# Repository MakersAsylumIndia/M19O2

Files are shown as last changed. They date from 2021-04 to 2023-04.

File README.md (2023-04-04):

# M19O2
DiY Oxygen Concentrator based on / inspired by the [OpenOx](https://github.com/hacklabkyiv/openox), [Marut](https://www.technido.com/marut), [RepRap](https://github.com/RepRapLtd/Oxygen-concentrator) and [Project Apollo](https://github.com/oxycon/ProjectApollo) platforms.

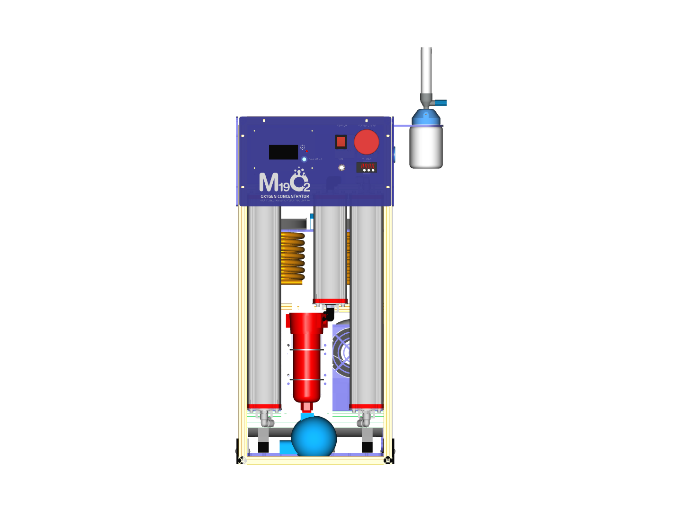
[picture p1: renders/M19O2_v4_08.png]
M19O2 render front


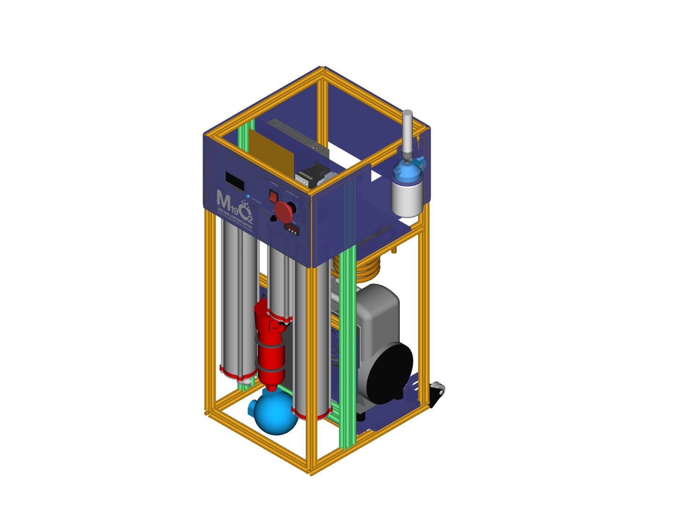
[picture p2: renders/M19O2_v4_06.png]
M19O2 render rear


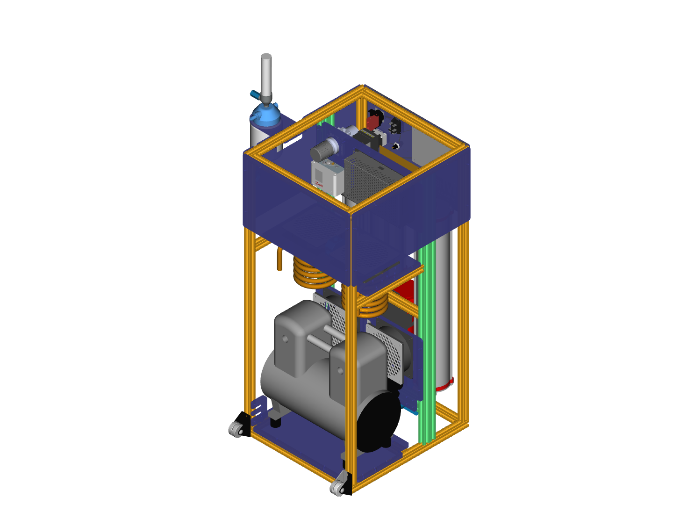
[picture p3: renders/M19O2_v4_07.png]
M19O2 render rear


## About

Read about the project on [Hackaday](https://hackaday.com/2021/04/26/indian-makers-respond-to-the-covid-19-pandemic-by-producing-oxygen-concentrators/).
Also check out the project on the [hackaday.io](https://hackaday.io/project/181201-m19o2-oxygen-concentrator) project page.

The **M19O2** Oxygen Concentrator is "Open Source Hardware" as certified by the [OSHWA](https://certification.oshwa.org/in000029.html).
OSHWA UID for the M19O2 is **IN000029**

<a href="https://certification.oshwa.org/in000029.html">OSHWA UID IN000029

## Contribute

You can contribute on the [Ketto fundraiser page](https://www.ketto.org/fundraiser/m19-oxygen-concentrators-make-in-india)

## Coordination lists

- [Notion workspace](https://www.notion.so/M-19-Collective-b44b9d8d7dd14d5d86d417facf0f4141) for the M19 collective.
- [M19O2 Master](https://docs.google.com/spreadsheets/d/1rJZ5P0rF2Or8yu0H8HEPz25RP8kTAXxbNVU87DqD-eM/edit#gid=0) sheet tracks the city-wise coordinators, tools, FAQs etc.
- [BOM M19O2](https://docs.google.com/spreadsheets/d/1gmmdXTP3EQk-4hCGVYj-FxzUMADlT8mw354VPmYt5A4/edit#gid=870920932) sheet lists the master Bill of Materials (BOM) along with city-wise BOM
- [Starting a community lab](https://docs.google.com/document/d/1oR9rhGmbcnoSBjzQCYwE9Anocvr0q5_VmuVkbnycx18/edit?usp=sharing) document and [Build List for Labs](https://docs.google.com/spreadsheets/d/1DynT9Mh8jcV9qHxwFuQxj1fcQQHj_v_ymwpoZD1L23g/edit?usp=sharing) sheet for lab onboarding information and coordination.

## Engineering

- [Labview testbench](engineering/software/M19-oxygen-concentrator-testbench) is a testbench executable developed by [Fracktal Works](https://github.com/FracktalWorks), useful for tuning the performance of your concentrator prototypes.
- [Computer-aided Design/Engineering](engineering/cad-cae) for design, version control and simulation data related to the M19O2 and its iterations. Committed to open-source and open-innovation.
- [Electronics](engineering/electronics) for all things electronics, including comprehensive design and development data of DIY [Oxygen Analyzers](engineering/electronics/oxygen_analysers) and other [subprojects](engineering/electronics/subprojects).

## How to use this repo

Open a terminal on your computer. Run

```bash
git clone https://github.com/MakersAsylumIndia/M19O2 && cd M19O2
git submodule update --init --recursive
```
The repository shall be available on your computer.
To periodically update the contents,

```bash
cd M19O2
git pull
git submodule update --init --recursive
```

## How to contribute to this repository

Fork this repository. You can find the command for this on the top-right of the webpage. This shall create a personal, updateable copy of this repository on your github account.

On your computer terminal, run

```bash
git clone https://github.com/<your-username>/M19O2 && cd M19O2
git submodule update --init --recursive
```
Add your contributions to this repository and save on github.

```bash
cd M19O2
git add .
git commit -m "<your-commit-message>"
git push origin
```

To contribute your work to the M19 Collective, open your repository in a browser and issue a pull request from your repository to the one at [Makers' Asylum](https://github.com/MakersAsylumIndia).

## License

Licenses

<a href="LICENSE.md">Open Source Licenses Facts</a>

#### Hardware
CERN Open Hardware License Version 2 - Strongly Reciprocal ([CERN-OHL-S-2.0](https://spdx.org/licenses/CERN-OHL-S-2.0.html)).

#### Software
MIT open source [license](http://opensource.org/licenses/MIT).

#### Documentation:
<br />This work is licensed under a <a rel="license" href="http://creativecommons.org/licenses/by/4.0/">Creative Commons Attribution 4.0 International License</a>.

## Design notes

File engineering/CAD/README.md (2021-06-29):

This folder is dedicated to M19O2 CAD files and version-control.

*Starting/Kickoff contents*
M19O2 - 
 * FCstd file (FreeCAD v0.19) and STEP/STL export formats
 * FCstd files for sub-projects such as sieve compression jig, sieve assembly, O2 sensor housing, Humidity sensor housing etc.

Oxikit_v22 - (DEPRECATED and moved to ARCHIVE)
 * F3D file (Fusion 360), 
 * STEP file (converted from F3D),
 * STL file (converted from STEP. for light *3d viewing* only) 
 * FreeCAD document (converted from STEP file. No feature model)

 * All individual OxiKit parts (exported from Fusion) as STEP files.

*TODO*
 * Convert F3D feature model appropriately to FreeCAD. --> Make freecad assembly with step files.
 * Set up framework for newer local design iterations and dimensional variants.
 * Integrate local subassembles/component information and product BoM management

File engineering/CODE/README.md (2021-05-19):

# M19_Oxikit_SD
Software development
Git submodule for M19 software development.
 
Submodule is currently in argo-1 repositories.

 *TODO General*
 * Create submodules under MakersAsylum git. Current submodules are linked to argo-1 repos. Argo-1, and others, can thereafter fork the submodules for their own development from MakersAsylum.
 * Add all software dev work here.

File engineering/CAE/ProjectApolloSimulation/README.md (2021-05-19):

Note: this repository contains the simulation code for Project Apollo

Please refer to the original repository for more details on Apollo: https://github.com/oxycon/ProjectApollo 

These files are for a simulation of pressure swing adsorption oxygen concentrator

# References

For numerical methods:
Haghpanah, et al "Multiobjective Optimization of a Four-Step Adsorption Process
for Postcombustion CO2 Capture Via Finite Volume Simulation"  Industrial & Engineering
Chemistry Research, 2013

For PSA operation:
Farooq, "Numerical Simulation of a Pressure Swing Adsorption Oxygen Unit"
Chemical Engineering Science, Vol 44, No 12, pp 2809-2816, 1989.

For constants for sieve material 5A and 13X
Mofarahi, "Comparision of Two Pressure Swing Adsorption Processes for Air Separation
Using Zeolite 5A and Zeolite 13X", Petroleum & Coal,  ISSN 1337-7027, 55 (3) 216-225, 2013.

# Software organization
```
psa.py         simulation module - provides a function simulate() and simulate_and_plot()
               which can be called to do the acutal simulation
params.py       sets the parameters (other files are available: params-apollo, etc.)
mylog.py       log file utilities
difference.py  finite volume and finite difference functions
simple_sim     early simulation that does not do any adsorption (ignore)
```
# Top level files
```
(these call simulate_and_plot() ) and run from the command line.
Use standard python command line options, use --h for help
single_sim     does a single simulation, demostrates usage of simulate_and_plot
optimize       Uses scipy optimization routines to optimize variable through search
annealing      Uses simulated annealing technique for same
monte_sim      Uses Monte Carlo technique for same
multiple_sim   Does a range of simulations
search_sim     Similar, tries to capture best result
jee_sim        Simulation of Jee paper parameters
```

# State Vars
The state variables in the system are:
For each container (1 and 2), each state variable in an (N,) array, where
N (=param.N) is the number of cells in the discretization of the PDE.  10 cells
works well, although higher accuracy is obtained with a much larger number.  All
the variables are in dimensionless values, that are normalized to generally be from
0-1, although they could exceed that.  For example, time is normalized so that the
initial velocity air flow takes 1 unit of time to travel across the container
bed, but the simulation might run for 100's of units of time.
```
   P:  Pressure of gas in bed
   T:  Temperature in bed (this version uses a contant T)
   Tw: Temperature of wall of bed (this version uses a constant Tw)
   xA: Adsorbed amount (mass/volume) of component A (Oxygen)
   xB: Adsorbed amount (mass/volume) of component B (Nitrogen)
   yA: partial concentration of component A (Oxygen) in bed (fraction 0-1)
   yB: partial concentration of component B (Nitrogen) in bed (fraction 0-1)
```
The product tank has 2 state variables:
```
  Pprod:  Pressure in tank
  yprod:  fraction of Oxygen in tank
```
# Modes
We have 6 modes to operate under:
```
                            COL1                    COL2
MODE     Switch 5-way valve                            
half==0 and 1.   Pressurize 1           pressurizing              Vent
half==0 and 2.   Produce 1              pressurize & output       Vent
Open cross valve
half==0 and 3.   CrossVent              Pressurize, out to COL2   Vent
Close Cross valve and Switch 5-way valve
half==1 and 1.   Pressure 2
half==1 and 2.   Produce 2
Open cross valve
half==1 and 3.   CrossVent 2
and repeat at top
```

# Observations

1. The cycle time must be short enough that the product (O2) tank can supply the
   desired flow rate without dropping the pressure too much.  At 5 LPM, a 2L tank
   at 3 bar abs can hold about 2*2/5*60 sec of product (48 sec).
2. The absorption rate of the seive material affects the rate of pressure growth
   in the tanks.  Thus the cycle time is dependent on the absorption rate of the
   material
3. A shorter cycle time could work, but the oxygen level grows slower (in cycles),
   as the pressure does not reach feed pressure by the end of the cycle (unless
   a larger orifice is used).  This might be OK, it just takes more than 7 cycles
   to reach steady state.
   See sims for 10 sec (real) cycle

# NOTES
You can use Inkscape to view and convert svg files. inkview comes with inkscape.

inkview <svg-files>
inkscape -z -w <width-in-pixels> -h <height-in-pixels> <svg-file> -e <png-file-name>

Inviracare XL cylinders are D=.083m, L=.355m
2 Liter bottle: D=0.10, L=.33

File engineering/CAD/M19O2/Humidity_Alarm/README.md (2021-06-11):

# M19O2 Humidity Alarm

  Reads a DHT-22 sensor attached in-line between the output of Dessicant Sieve and input of high pressure regulator of the M19O2 Oxygen Concentrator.
  This tells us how much moisture is entering the Zeolite Dessicant Sieves.
  
  * HIGH = >50%rH = Red Blinking LED + Buzzer
  * MID = <50%rH, >30%rH = Red Blinking LED
  * LOW = <30%rH, >15%rH = Blinking Green LED
  * AWESOME = <15%rH = Steady Green LED

  The DHT22 can only measure under ambient pressure (1 ATM), so we tap off the high pressure line and feed air through restrictors (orifices) in to an air-sealed chamber containing the DHT-22.
  The output from the air sealed chamber feeds back in to the main line, again through a similar restrictor orifice.

  In a later iteration, a flushing solenoid valve can be connected which will purge incomming air back to atmosphere until humidity level falls below a set percentage, thus preventing humid air from reaching the sieves.

  This code is in the public domain.

  Hardware and code by Anool J M (@anool) and Narender Sharma of Maker's Asylum  

  https://github.com/MakersAsylumIndia/M19_OxiKit/tree/main/engineering/M19Oxykit_humidity_alarm

=======

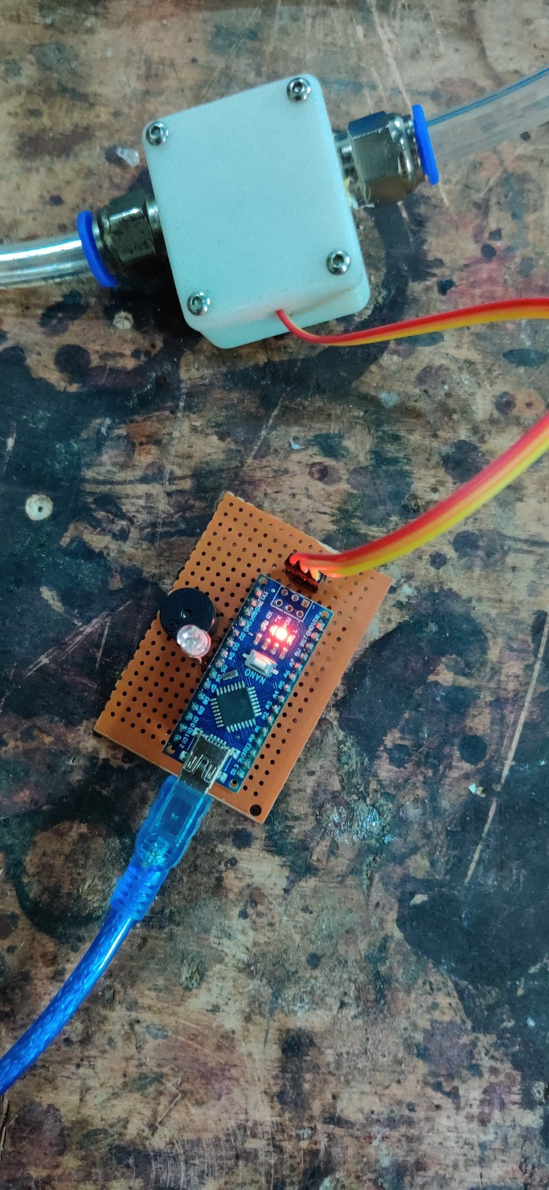
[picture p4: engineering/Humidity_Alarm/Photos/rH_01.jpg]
Humidity Alarm photo 1


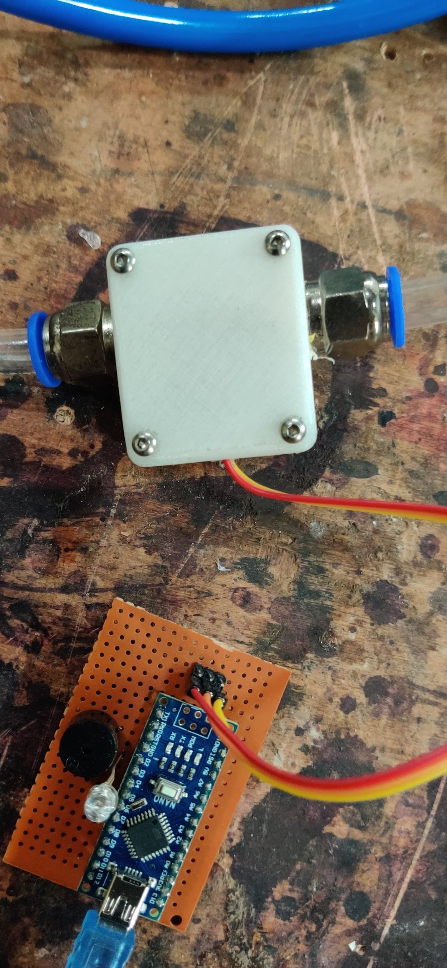
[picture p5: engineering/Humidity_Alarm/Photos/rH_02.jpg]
Humidity Alarm photo 2


License
-------
[CERN Open Hardware Licence v1.2 ]

[CERN Open Hardware Licence v1.2 ]:http://www.ohwr.org/attachments/2388/cern_ohl_v_1_2.txt

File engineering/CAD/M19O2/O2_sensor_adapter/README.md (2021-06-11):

# M19O2 Oxygen Sensor Adapter

  3D printed adaptor to connect an Envitec OOM-Series O2 sensor at the output of the M19O2 Oxygen Concentrator
  
  This design is in the public domain.

  Hardware design by Anool J M (@anool) of Maker's Asylum.

  https://github.com/MakersAsylumIndia/M19_OxiKit/tree/main/engineering/O2_sensor_adapter

=======

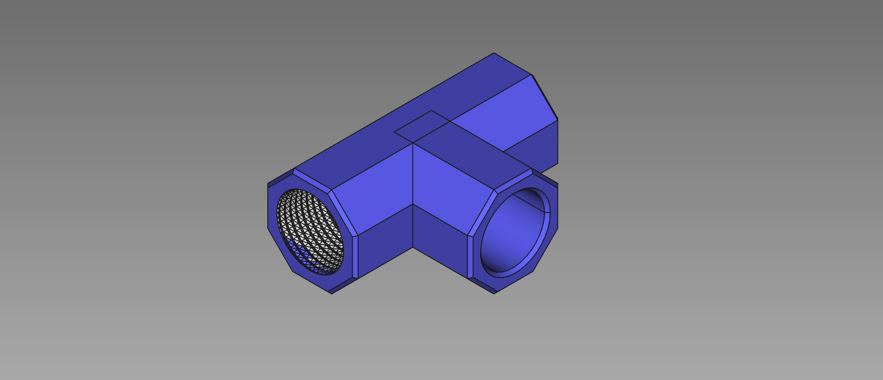
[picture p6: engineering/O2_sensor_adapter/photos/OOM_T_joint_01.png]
O2 sensor mount photo 1


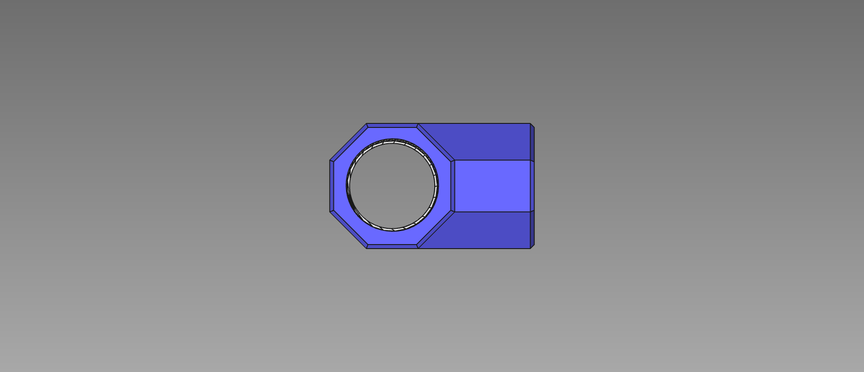
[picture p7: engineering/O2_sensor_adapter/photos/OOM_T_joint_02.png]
O2 sensor mount photo 2


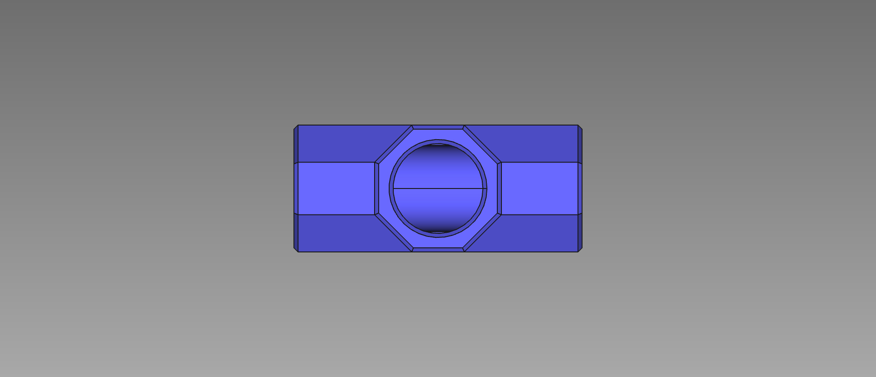
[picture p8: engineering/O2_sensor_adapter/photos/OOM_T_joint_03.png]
O2 sensor mount photo 3


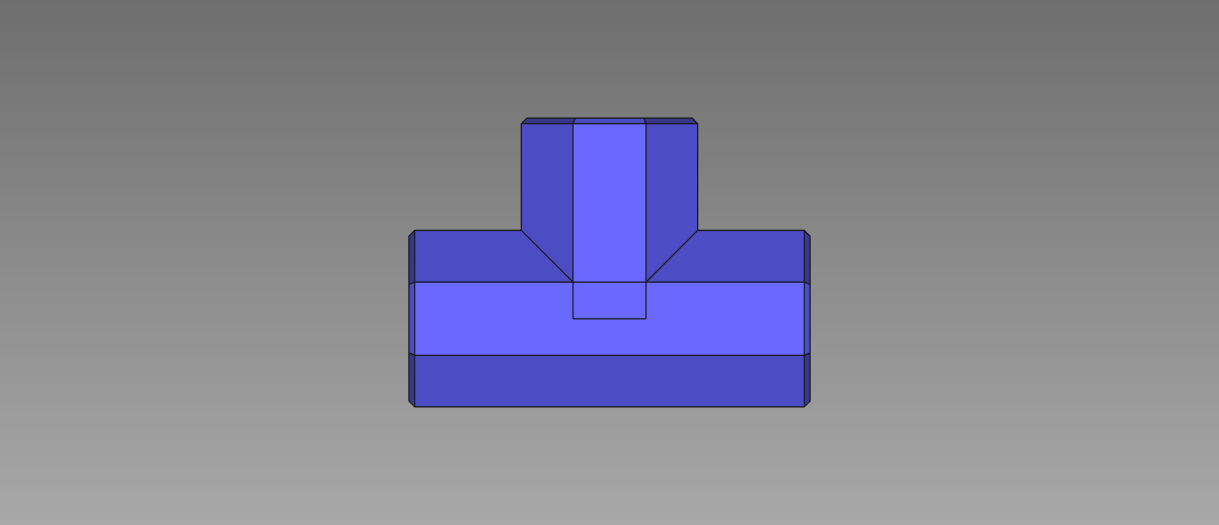
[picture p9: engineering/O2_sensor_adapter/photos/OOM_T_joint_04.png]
O2 sensor mount photo 4


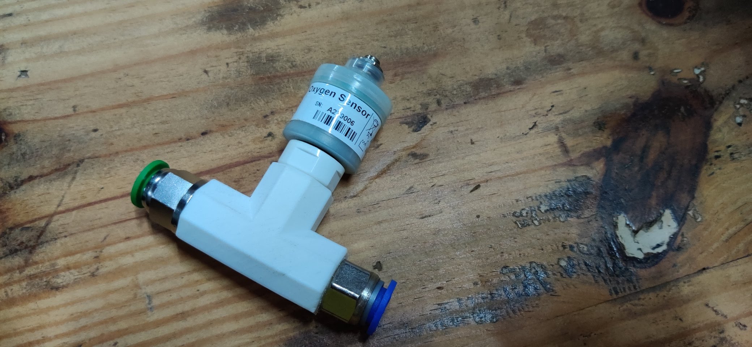
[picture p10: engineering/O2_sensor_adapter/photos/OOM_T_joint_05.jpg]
O2 sensor mount photo 5


License
-------
[CERN Open Hardware Licence v1.2 ]

[CERN Open Hardware Licence v1.2 ]:http://www.ohwr.org/attachments/2388/cern_ohl_v_1_2.txt

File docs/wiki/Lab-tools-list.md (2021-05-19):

## Tools list for labs

This list is curated from the [Lab Tools Requirement](https://docs.google.com/spreadsheets/d/1DynT9Mh8jcV9qHxwFuQxj1fcQQHj_v_ymwpoZD1L23g/edit#gid=1782181776) sheet.

Contributions to improve this Wiki page are welcome.

TODO: add e-store links to each tool.

| Tool Name | Required for process | Alternative tools | Notes | Video Reference | Image Reference |
| ------ | ------ | ------ | ------ | ------ | ------ |
| Oxygen Analyzer | Quality Assurance  |  | Ensure Quality of oxygen (% concentration)  meets requirements. Also ensure both sieves are working at expected | [https://www.youtube.com/watch?v=cm3BnYiPxQ0](https://www.youtube.com/watch?v=cm3BnYiPxQ0) |  [https://tinyurl.com/Oxygen-Testor](https://tinyurl.com/Oxygen-Testor)|
| Electric Sander | Cleaning/smoothing wood and PVC parts | Sand paper/ Emery paper | Sand paper (for wood, PVC, various grits) and Emery paper (for metal, various grits) |  | |
| Soldering Iron | Electronics / Electrical wiring | Solder Station |  |  |  |
| Electrical Tape | for insulation of wire joints | [Wire Nut / Wire Connector](https://en.wikipedia.org/wiki/Twist-on_wire_connector) |  |  |  |
| Electrical Drill | Wood work  | Hand drill |  |  |  |
| Drill Bits- various sizes | Wood work  |  |  |  |  |
| 1" Forschener Bit | for making large holes in wood | aka Hole saw / Hole cutter etc |  |  |  |
| Safety Equipment |  |  | Gloves, Eye glasses etc |  |  |
| Wire Strippers | Electronics / Electrical wiring |  |  |  |  |
| Screw Drivers | Assembly |  |  |  |  |
| Wrenches | Assembly |  |  |  |  |
| Plumbers Tape | for thread sealing of pneumatic fittings | aka Teflon Tape |  |  |  |
| Tubing Cutter | flexible pneumatic tube cutting |  |  |  |  |
| Saw for PVC Cutting | PVC cutting |  |  |  |  |
| Hose Clamps |  |  |  |  |  |
| PPE Kit for build team |  |  |  |  |  |
| Table for build |  |  |  |  |  |
| Electrical extensions with multi plug |  |  |  |  |  |
| General purpose knife / box cutter etc | Multiple |  |  |  |  |
| Deburring tool | For deburring cut PVC pipes | general purpose knife or sand paper |  |  |  |
| Cleaning cloth rags | Multiple |  | to wipe excess glue and keep things clean |  |  |
| Rubber Gloves | PVC parts assembly |  |  |  |  |
| Adjustable spanner / pipe wrench | PVC parts assembly | cloth + welding gloves + brute strength |capable of 3" piping work  |  |  |
| Adjustable Strap wrench | PVC parts assembly | cloth + welding gloves + brute strength | aka Belt Wrench |  |  |
| Snipper clips (Tin snipper) | PVC parts assembly |  | for cutting 3" drain to size. Not neded if those parts are 3D printed |  |  |
| Scissors | Multiple |  |  |  |  |
| SuperGlue | PVC parts assembly |  | for attaching mesh |  |  |
| Vernier Caliper | Sieve assembly |  | to mark level upto which Zeolite needs to be filled (after comaction) | [https://youtu.be/kibjku2GYq0?t=257](https://youtu.be/kibjku2GYq0?t=257) |  |
| Vibratory mechanism  | Zeolite compaction |  | Many approaches to this - use a pneumatic impact hammer, a vibratory table, any reciprocating hand tool (sander, buffing etc).  Vacuum also works well - using either a Shop Vac or maybe a regular vacuum cleaner) | [https://youtu.be/kibjku2GYq0?t=441](https://youtu.be/kibjku2GYq0?t=441) |  |

Ported by [@nirmaljeffrey](https://github.com/nirmaljeffrey).

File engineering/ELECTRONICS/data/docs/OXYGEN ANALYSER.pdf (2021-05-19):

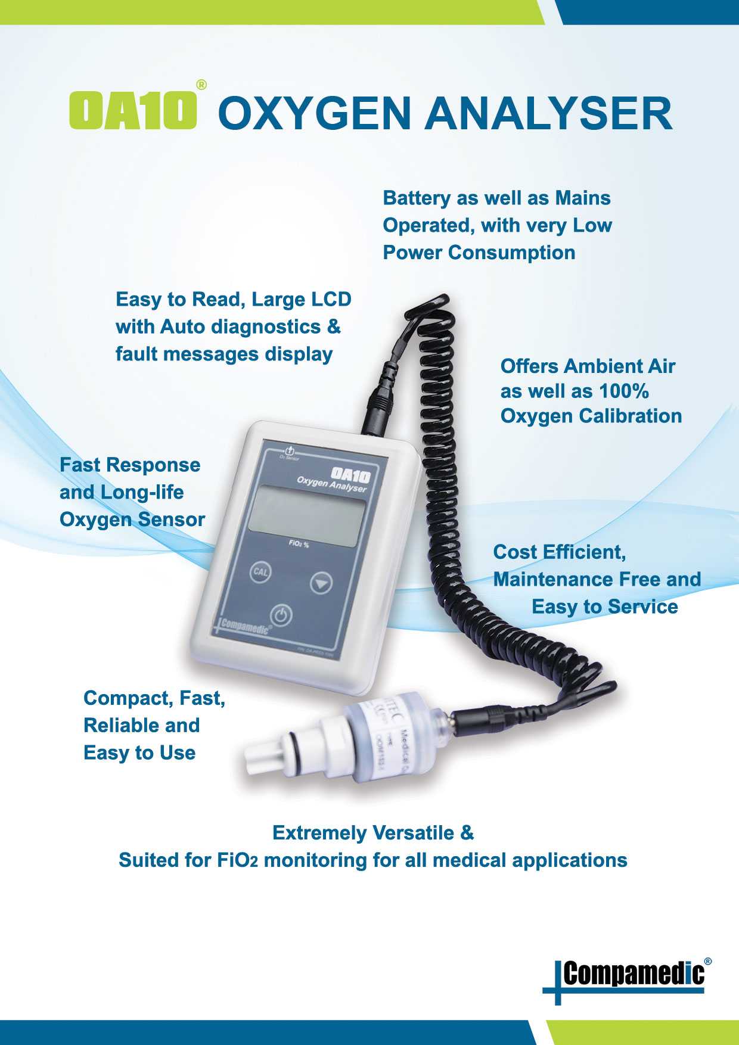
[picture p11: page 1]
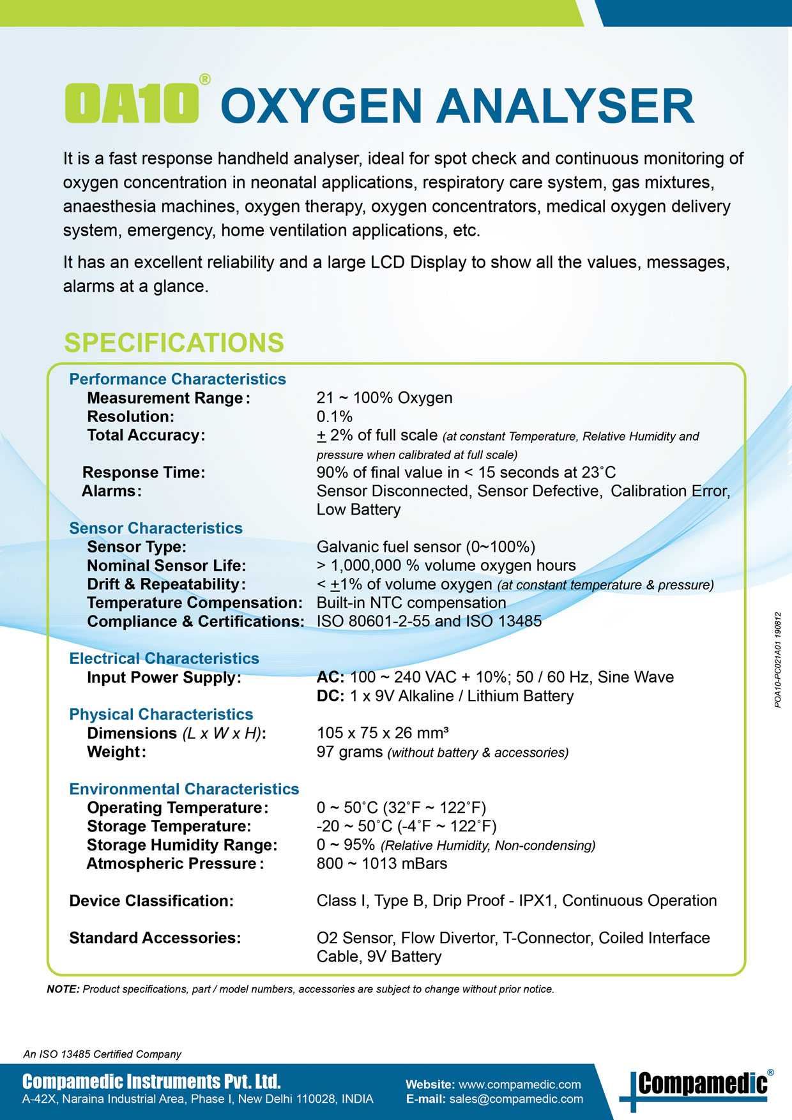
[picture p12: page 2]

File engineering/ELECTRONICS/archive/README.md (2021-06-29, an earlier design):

# Oxikit_Brain_Wiring_Simplified

### This is the simplified schematic for understanding the OxiKit Brain Circuit(Microcontroller based Controller for Oxikit Oxygen Concentrator).

### ECAD Software Used: KiCAD (Open Source ECAD Software)

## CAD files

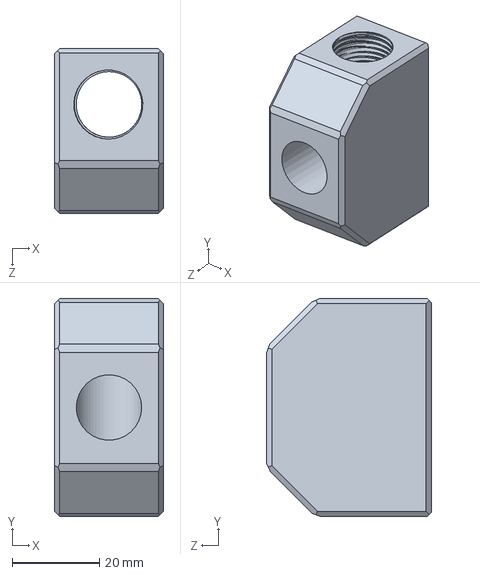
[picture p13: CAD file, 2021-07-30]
engineering/CAD/M19O2/O2_sensor_adapter/T-joint_Vaibhav/M19O2_v4_assembly-O2_sensor.SLDPRT
25.0 x 50.0 x 37.8 mm

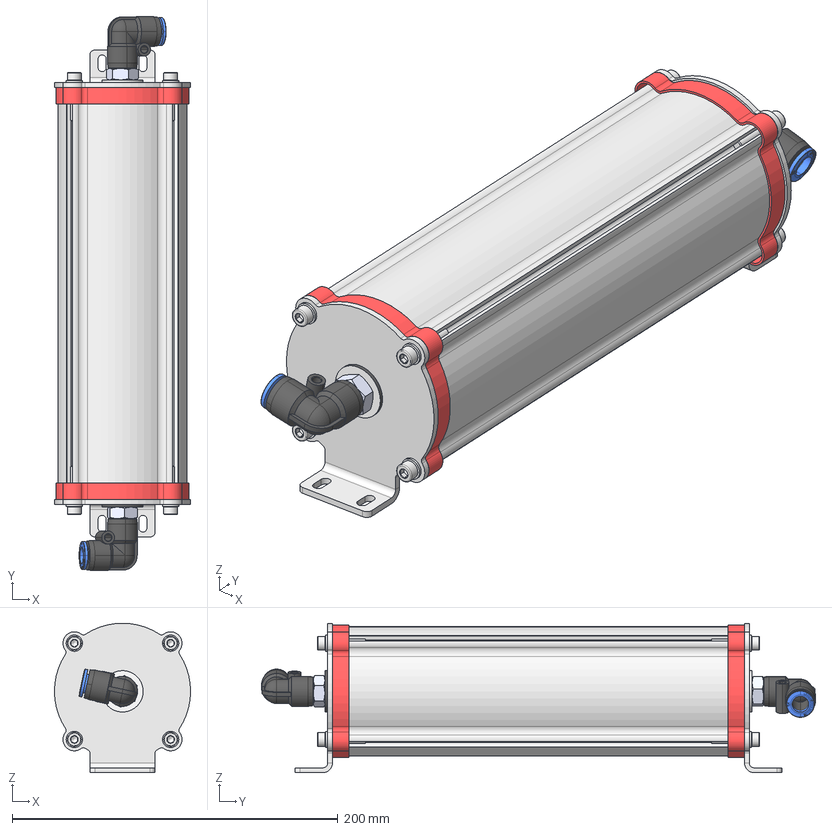
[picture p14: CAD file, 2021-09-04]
engineering/CAD/M19O2/Sieve_Assembly/surge_tank_assy.step
83.6 x 340.2 x 91.8 mm
sieve_body
screws
gasket_(Mirror_#4)
gasket
screws001

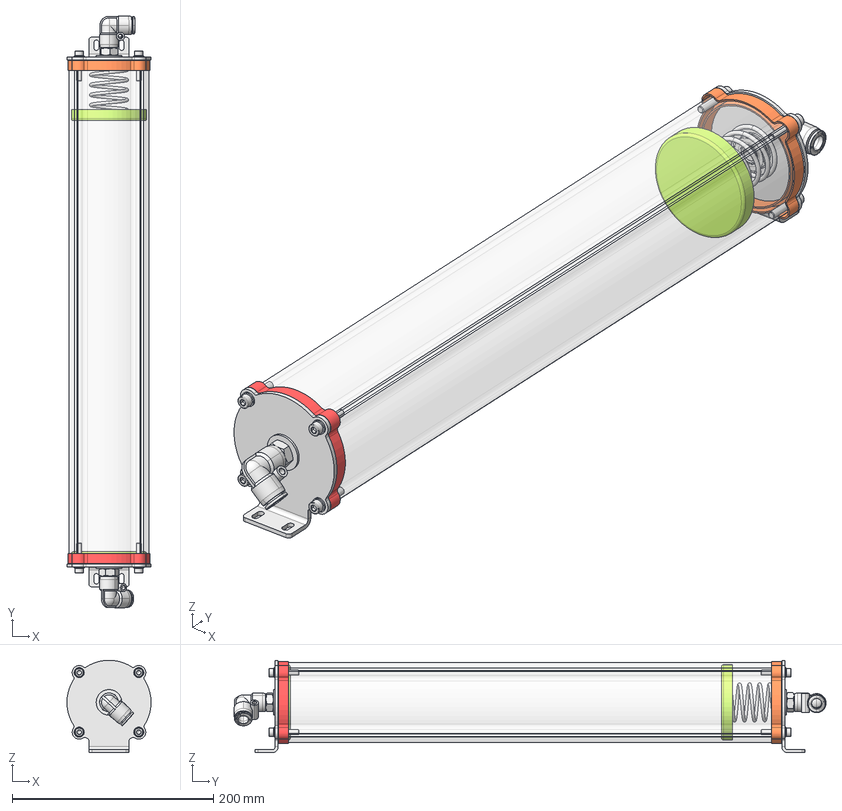
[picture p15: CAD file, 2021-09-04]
engineering/CAD/M19O2/Sieve_Assembly/sieve_assembly_v3.FCStd
83.6 x 587.8 x 91.8 mm
feltpad_filter
feltpad_filter (Mirror #3)
gasket
sieve_body
endcap
drain_cover
drain_cover (Mirror #4)
endcap (Mirror #4)
gasket (Mirror #4)
screws
screws001
endcap_fittings
endcap_fittings001
Spring

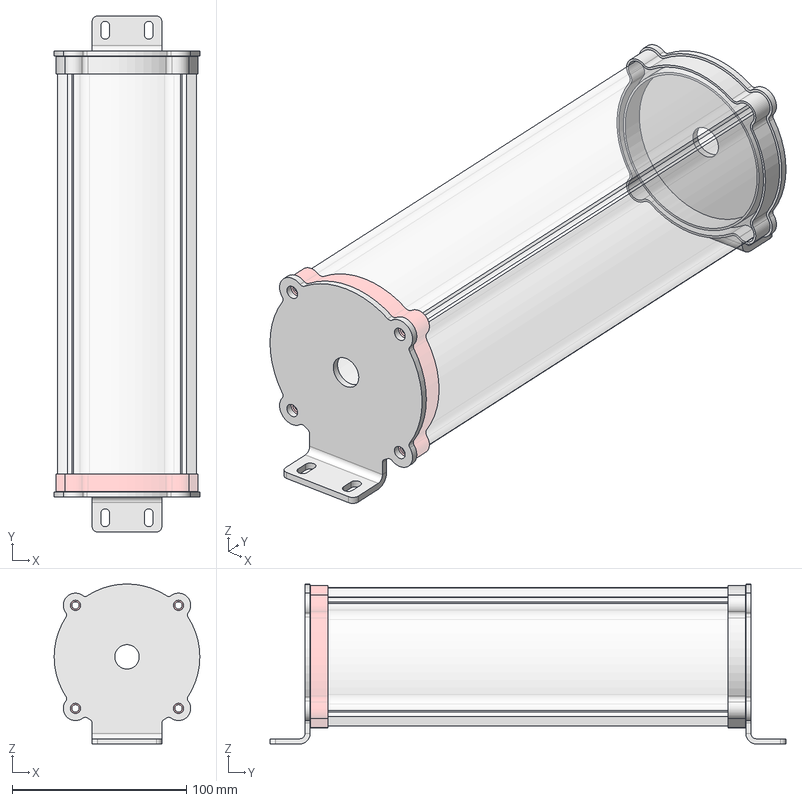
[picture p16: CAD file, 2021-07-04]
engineering/CAD/M19O2/Sieve_Assembly/surge_tank_assembly_v3.FCStd
83.6 x 296.0 x 91.8 mm
gasket
sieve_body
endcap
endcap (Mirror #4)
gasket (Mirror #4)

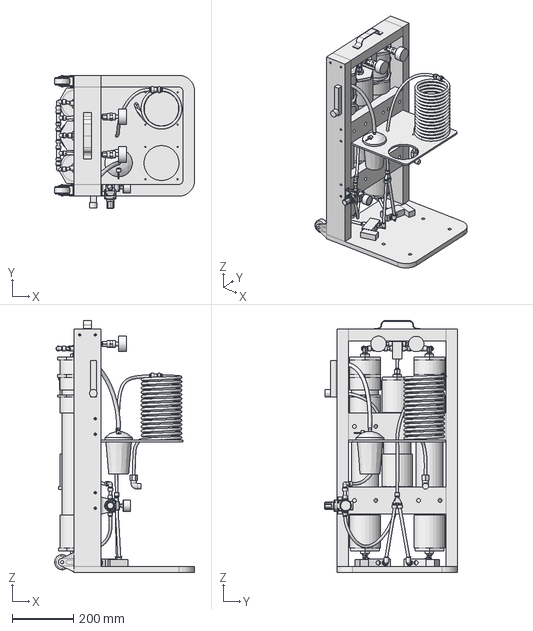
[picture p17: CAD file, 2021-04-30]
engineering/cad-cae/cad/OxiKit_v22/OxiKit_v22.FCStd
457.2 x 434.3 x 821.7 mm

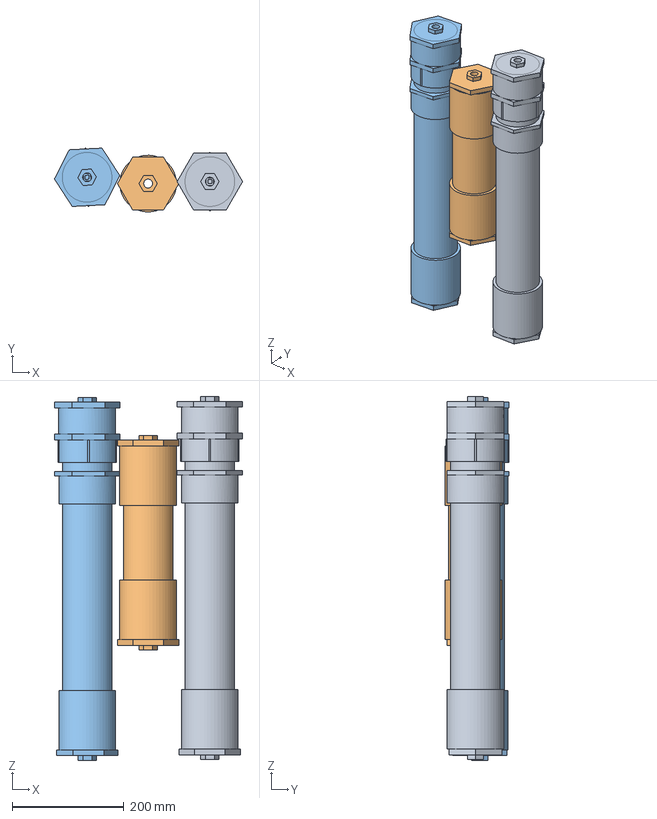
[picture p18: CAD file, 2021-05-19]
engineering/cad-cae/cad/OxiKit_v22/Parts/Assemblies/tanks.FCStd
337.0 x 114.4 x 651.5 mm
Seive001
SurgeTank001
Seive002

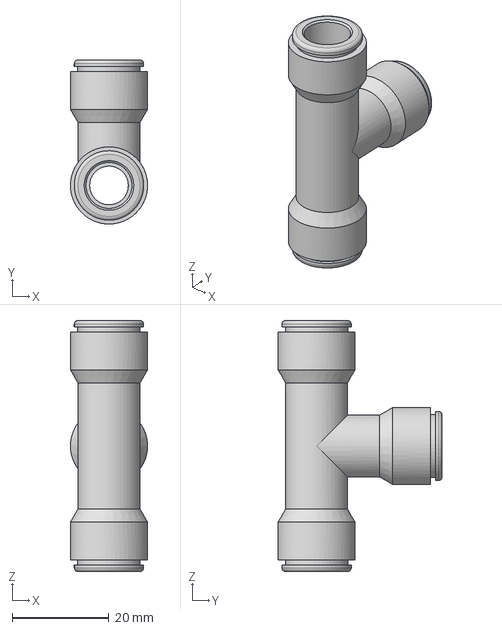
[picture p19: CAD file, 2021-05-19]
engineering/cad-cae/cad/OxiKit_v22/Parts/Fittings/0.375_TPush.step
16.0 x 34.0 x 52.0 mm

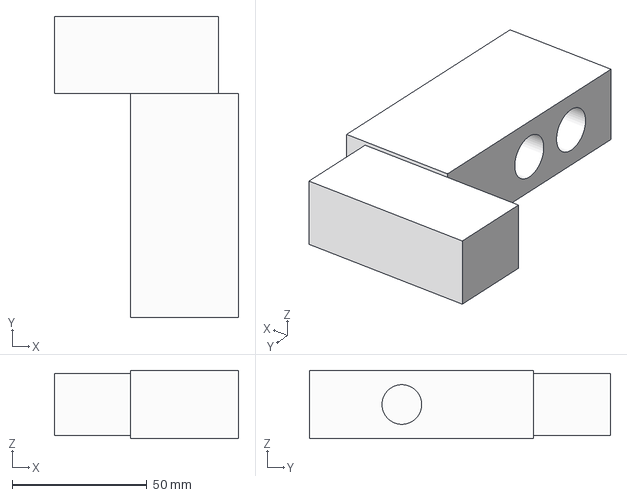
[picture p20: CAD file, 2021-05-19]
engineering/cad-cae/cad/OxiKit_v22/Parts/Fittings/Valves/ThreeWay_0.375_FPT.step
68.3 x 111.8 x 25.4 mm

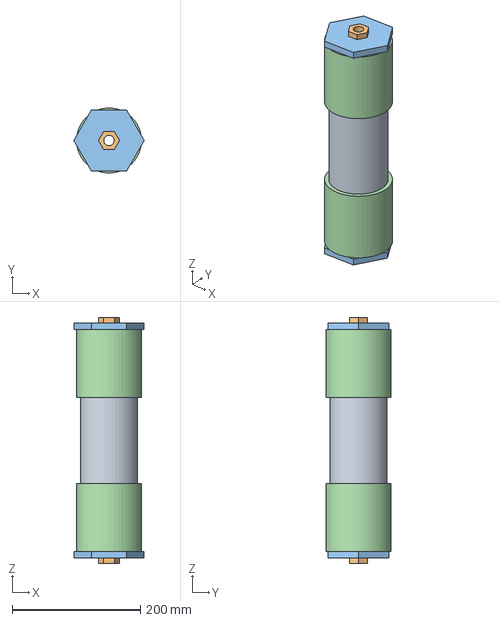
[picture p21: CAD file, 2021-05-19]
engineering/cad-cae/cad/OxiKit_v22/Parts/Tanks/SurgeTank.step
110.0 x 101.6 x 384.0 mm
Pipe9in
3/4inTo3/8inReducer x 2

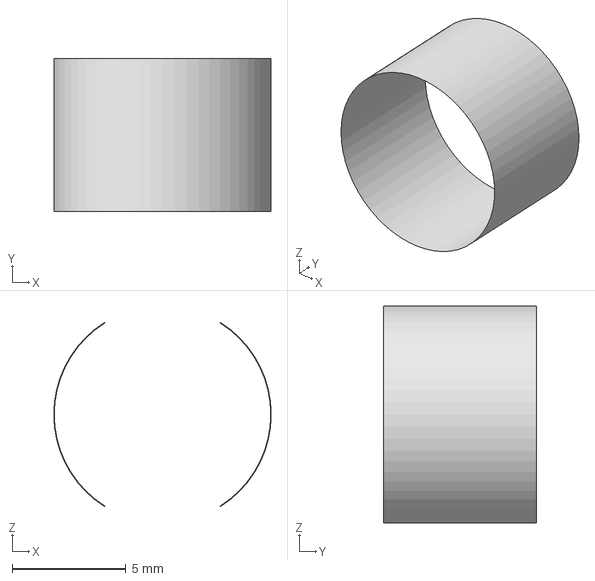
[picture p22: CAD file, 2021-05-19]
engineering/cad-cae/cad/OxiKit_v22/Parts/Tubes/tube (6).step
9.53 x 6.69 x 9.52 mm

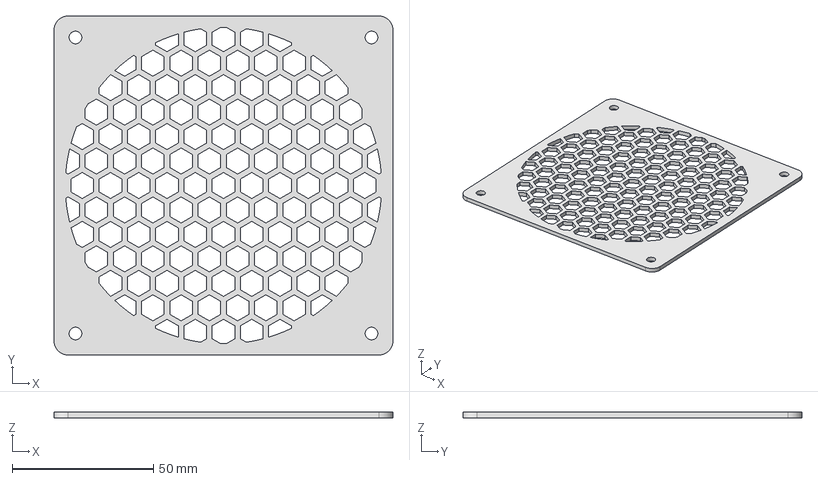
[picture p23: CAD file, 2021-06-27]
engineering/CAD/M19O2/120mm_fan_grill/120mm_fan_grill.step
120.0 x 120.0 x 2.00 mm

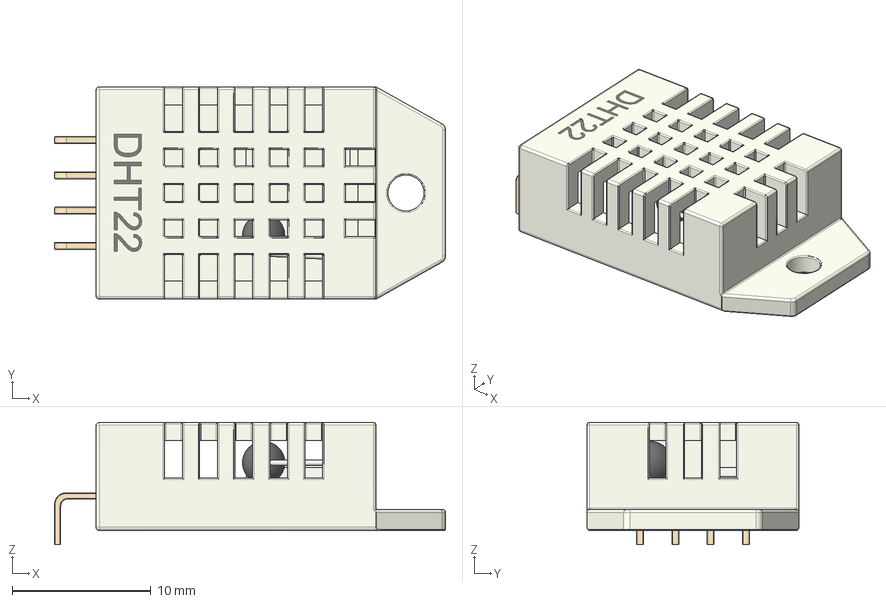
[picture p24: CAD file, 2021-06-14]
engineering/CAD/M19O2/Humidity_Alarm/DHT22_pcb/3d_models/DHT22_T_sensor.step
28.2 x 15.3 x 8.80 mm

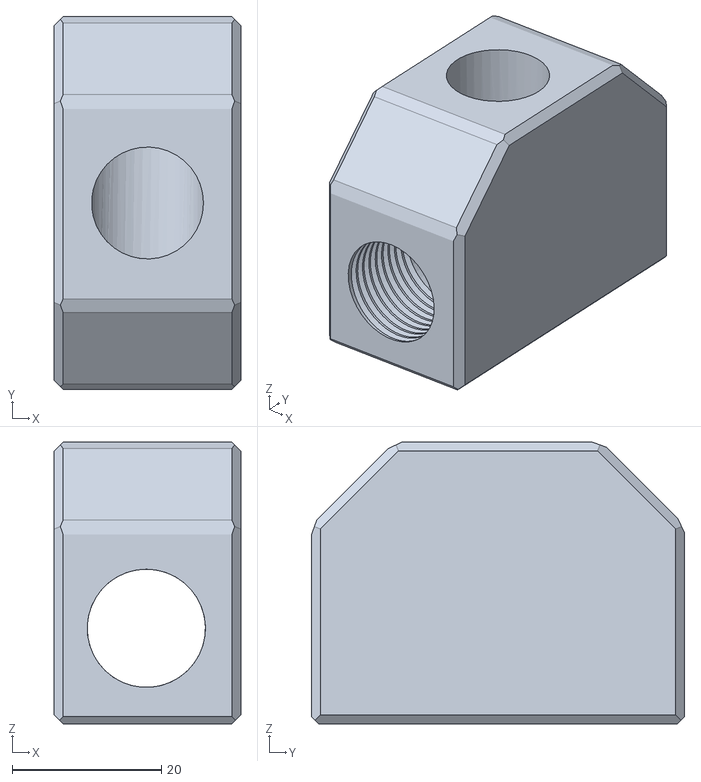
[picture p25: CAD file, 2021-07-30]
engineering/CAD/M19O2/M19O2_assembly/3D_prints/oxysensor block.stl
25.0 x 50.0 x 37.8

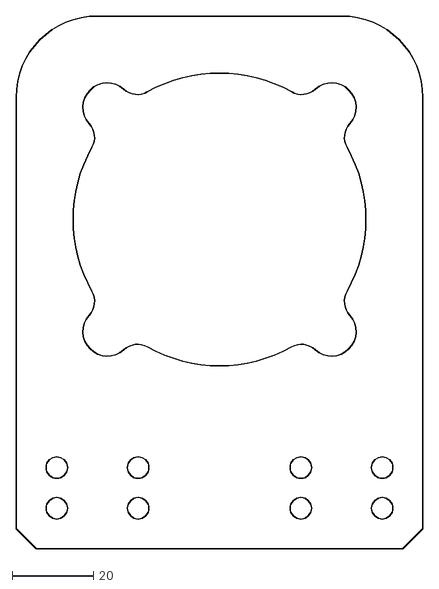
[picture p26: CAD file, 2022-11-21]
engineering/CAD/M19O2/M19O2_assembly/Laser_Cut_Parts/acr_sieve_bracket_dia71-02.dxf
100.0 x 131.0

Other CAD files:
engineering/cad-cae/cad/OxiKit_v22/Parts/Assemblies/OxiKit_v22_Assembly.FCStd
engineering/CAD/M19O2/Sieve_Assembly/sieve_assy_B.step
engineering/CAD/M19O2/Sieve_Assembly/sieve_assy_A.step
engineering/cad-cae/cad/OxiKit_v22/Parts/Frame/Brace.step
engineering/CAD/M19O2/120mm_fan_grill/120mm_fan_baffle.FCStd
engineering/CAD/M19O2/Humidity_Alarm/DHT22_pcb/3d_models/DHT22_sensor.step
engineering/CAD/M19O2/Humidity_Alarm/sensor_housing/FESTO_533221QB1438UM/533221 QB-1_4-3_8-U-M.igs
engineering/CAD/M19O2/Humidity_Alarm/sensor_housing/FESTO_533221QB1438UM/533221 QB-1_4-3_8-U-M.stp
engineering/CAD/M19O2/Humidity_Alarm/sensor_housing/FESTO_533224QB3838UM/533224 QB-3_8-3_8-U-M.igs
engineering/CAD/M19O2/Humidity_Alarm/sensor_housing/FESTO_533224QB3838UM/533224 QB-3_8-3_8-U-M.stp
engineering/CAD/M19O2/Humidity_Alarm/sensor_housing/FESTO_533226QB1238UM/533226 QB-1_2-3_8-U-M.igs
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

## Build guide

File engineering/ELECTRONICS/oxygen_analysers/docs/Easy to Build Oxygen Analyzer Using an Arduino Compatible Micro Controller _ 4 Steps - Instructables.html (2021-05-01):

Log In (https://www.instructables.com/account/login/) | Sign Up (https://www.instructables.com/account/register/)

Instructables instructablescircuits (https://www.instructables.com/circuits/)Projects (https://www.instructables.com/circuits/projects/)Contests (https://www.instructables.com/contest/)

Enter search term

# Easy to Build Oxygen Analyzer Using an Arduino Compatible Micro Controller

By akurk (https://www.instructables.com/member/akurk/) in Circuits (https://www.instructables.com/circuits/)Arduino (https://www.instructables.com/circuits/arduino/projects/)

81,136

92

36

license

DownloadFavorite

## Introduction: Easy to Build Oxygen Analyzer Using an Arduino Compatible Micro Controller

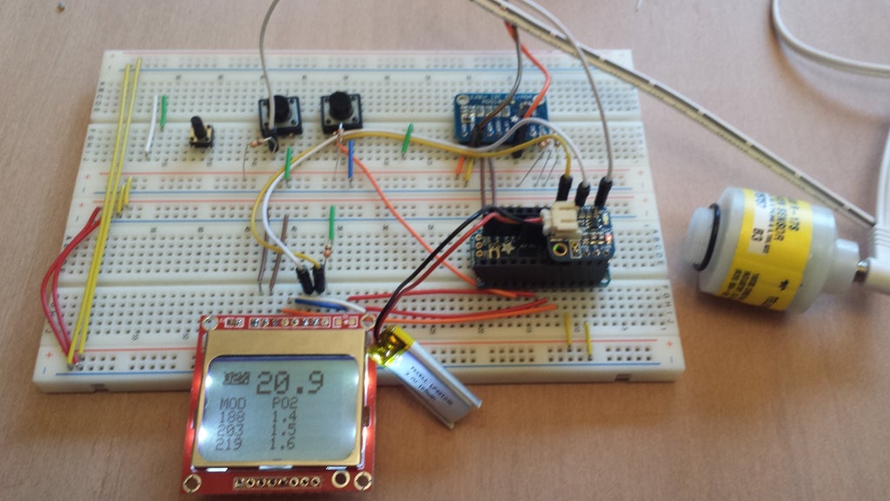
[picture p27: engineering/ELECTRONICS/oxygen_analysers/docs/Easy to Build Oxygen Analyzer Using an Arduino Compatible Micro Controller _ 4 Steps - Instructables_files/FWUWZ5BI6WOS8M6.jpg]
Easy to Build Oxygen Analyzer Using an Arduino Compatible Micro Controller


As a builder of gadgets and a scuba diver I have been trying to build an oxygen analyzer for a bit now. The big problem is that most micro controllers can’t read the mv that the sensor puts out. I played with opamps, but never got it to work properly. Finally I found the Texas Instruments ads1015, an analog to digital convertor chip “adc”. Adafruit makes a nice breakout board to make your life easier.

Now I only need a micro controller, an LCD screen, an oxygen sensor, a push buttons and like 9 resistors or so and I got yourself an oxygen analyzer.

Add TipAsk QuestionCommentDownload

## Step 1: Shopping List

Below are the components and parts with the links to where you can buy them

- Adafruit Pro Trinket 3v micro controller https://www.adafruit.com/products/2010
- Adafruit Lipo backpack charger for the Pro trinket with battery https://www.adafruit.com/product/2124
- Adafruit ads1015 breakout board https://www.adafruit.com/product/1083
- Nokia 5110/3310 monochrome LCD https://www.adafruit.com/product/338
- 7 10k ohm resistors
- 1 300 ohm resistors
- 1 push buttons
- 1 mono mini headphone plug
- Hookup wire
- Audio Jack - 3.5mm (Panel Mount) https://www.sparkfun.com/products/11154/
- Teledyne R17 O2 Sensor http://www.oxycheq.com/analyzers-sensors/sensors/...
- Sensor Cable *2 Foot* http://www.oxycheq.com/analyzers-sensors/accessor...
- Sensor Tee http://www.oxycheq.com/analyzers-sensors/accessor...

Add TipAsk QuestionCommentDownload

## Step 2: Connecting It All Together

Connecting It All Together (https://content.instructables.com/ORIG/FT2/KPBB/I6WOSFU1/FT2KPBBI6WOSFU1.png?auto=webp&frame=1&width=1024&fit=bounds&md=ee0385b7e96b191716b874ea6c53e369)

ADS1015

VDD Pin to 3.3v

GRD Pin to Ground

SCL Pin to A5 Pro Trinket

SDA Pin to A4 Pro Trinket

A0 Pin to Connected to the Audio Jack - O2 Sensor + pole

A1 Pin to Pull up Resistor 10K

A2 Pin to Pull up Resistor 10K

A3 Pin to Pull up Resistor 10K

Nokia display

VCC Pin to 3.3v

GRD Pin to Ground

SCE Pin to D8 Pro Trinket

RST Pin to D6 Pro Trinket

D/C Pin to D5 Pro Trinket

DN(MOSI) Pin to D11 Pro Trinket

SCLK Pin to D13 Pro Trinket

LED Pin to 200 ohm resistor to 3.3 V

Push Button

1 pin to Ground

2 Pin to D3 and a 10k pull-up resistor to 3.3v

Lipo Backpack

G Pin to Grd on Pro Trinket

3V 3V Pro Trinket

Pro Trinket

All the connections to the pro trinket are described in the above descriptions. I have added one 10k ohm pullup resistor to the RX pin. The Pro Trinket has the habit to sometimes hang on boot. This pullup resistor seems to remedy this. Why?..... Don’t know, a much smarter tinkerer on one of the Adfruit forums told me this piece of wisdom.

Note

The Lipo Backpack is the power source for the project. Every 3v connection needs to be connected to the Lip Backpack 3v and all the Ground connections need to be connected to the Lipo Backpack Ground including the audio jack witch is connected to the Ground of the Oxygen Sensor.

Add TipAsk QuestionCommentDownload

## Step 3: The Code

All the libraries used are from Adafruit and are easy to download from their site at www.adafruit.com. The formula for calculation the O2 % is simple.

(current mv from sensor / mv from sensor in the air) *20.9.

The only thing you need to do is store the "mv from sensor in the air" value in a variable before you try to analyze any gas. I do this in setup routine of my sketch or when you press the push button. Just download this zip file and upload the sketch to your pro trinket.

### Attachments

- download {{ file.name }} o2AnalyzerSample.zip (https://content.instructables.com/ORIG/FA2/8HLS/I6WOSCX6/FA28HLSI6WOSCX6.zip)
  Download (https://content.instructables.com/ORIG/FA2/8HLS/I6WOSCX6/FA28HLSI6WOSCX6.zip)

Add TipAsk QuestionCommentDownload

## Step 4: Finishing Toughes

Finishing Toughes (https://content.instructables.com/ORIG/FPO/PNB4/I6WOSHR0/FPOPNB4I6WOSHR0.jpg?auto=webp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)

To complete the project I put all the components in an enclosure and added 5v Regulator like a the 7805T witch I connected to the 5V in pin and the ground pin on the Lipo backpack to charge the battery.

I also added some code to calculate the maximum operating depth “mod” of the analyzed gas for a PO2 of 1.4,1.5, and 1.6

Formula for Imperial “Feet”

mod= ((po2/fraction of gass)-1)*33

Formula for Metric “Meter”

mod= ((po2/fraction of gas)-1)*10;

I also added a button so I could create a menu to select your mod unit “Meter or Feet”. To prolong the battery life I made it so that you can turn the backlight on the LCD display on and off.

I could show you how to do these things but figuring this stuff out is half the fun. If you get stuck I can help a little. If you know how to improve on the project please let me know as it is always good to learn new things.

Add TipAsk QuestionCommentDownload

## Be the First to Share

Did you make this project? Share it with us!

I Made It!

## Recommendations

AutoStrummer (https://www.instructables.com/AutoStrummer/)

AutoStrummer (https://www.instructables.com/AutoStrummer/) by JacobStambaugh (https://www.instructables.com/member/JacobStambaugh/) in Gadgets (https://www.instructables.com/circuits/gadgets/projects/)

4 409

2.1 Bluetooth Sound System - Fully Printable (https://www.instructables.com/21-Bluetooth-Sound-System-Fully-Printable/)

2.1 Bluetooth Sound System - Fully Printable (https://www.instructables.com/21-Bluetooth-Sound-System-Fully-Printable/) by EH_Design (https://www.instructables.com/member/EH_Design/) in Audio (https://www.instructables.com/circuits/audio/projects/)

1 662 36K

3 Ways to Make Cardboard PinBall Sensors (https://www.instructables.com/3-Ways-to-Make-Cardboard-PinBall-Sensors/)

3 Ways to Make Cardboard PinBall Sensors (https://www.instructables.com/3-Ways-to-Make-Cardboard-PinBall-Sensors/) by TechnoChic (https://www.instructables.com/member/TechnoChic/) in Sensors (https://www.instructables.com/circuits/sensors/projects/)

55 14K

Art Glove (https://www.instructables.com/Art-Glove/)

Art Glove (https://www.instructables.com/Art-Glove/) by JordanKDenn (https://www.instructables.com/member/JordanKDenn/) in Wearables (https://www.instructables.com/circuits/wearables/projects/)

26 13K

### Toys & Games Contest

- Toys & Games Contest (https://www.instructables.com/contest/toysgames2021/)

### Big vs Small Challenge

- Big vs Small Challenge (https://www.instructables.com/contest/bigvssmall/)

### Fix It Challenge

- Fix It Challenge (https://www.instructables.com/contest/fixit2021/)



Add Tip Ask Question Post Comment

We have a be nice policy.
Please be positive and constructive.

 Add Images  Post

## 36 Comments

0

joker14115 (https://www.instructables.com/member/joker14115/)

joker14115 (https://www.instructables.com/member/joker14115/)

4 months ago

ReplyUpvote

hello dear
i cant under stand ur sketch
it seems not complete and is for just callibrating sensor,
how do u know what percentage is o2 with current mv of sensor
it must be a function

0

constbad (https://www.instructables.com/member/constbad/)

constbad (https://www.instructables.com/member/constbad/)

7 months ago

ReplyUpvote

Please mention If someone did this instrument. How much it costs ? The links with sensor îs not more available . Could You mention other links ? Thanks.
If somebody knows a similar circuit for oxigen monitorizing please mention it here or on email : constbad@gmail.com. thanks

0

surojit191 (https://www.instructables.com/member/surojit191/)

surojit191 (https://www.instructables.com/member/surojit191/)

Question 7 months ago

AnswerUpvote

CAN I GET SINGLE LINE CIRCUIT DIAGRAM OF THE ABOVE PROJECT

0

jrgonaut (https://www.instructables.com/member/jrgonaut/)

jrgonaut (https://www.instructables.com/member/jrgonaut/)

Question 9 months ago

AnswerUpvote

Hi! Can I turn this into a controller as well?

1

rajesh197219 (https://www.instructables.com/member/rajesh197219/)

rajesh197219 (https://www.instructables.com/member/rajesh197219/)

Question 10 months ago on Step 2 (https://www.instructables.com/Easy-To-Build-Oxygen-Analyzer-Using-An-Arduino-Com/#step2)

AnswerUpvote

can you send the circuit diagram and some fundamental calculation

1

SaeidD1 (https://www.instructables.com/member/SaeidD1/)

SaeidD1 (https://www.instructables.com/member/SaeidD1/)

11 months ago on Step 3 (https://www.instructables.com/Easy-To-Build-Oxygen-Analyzer-Using-An-Arduino-Com/#step3)

ReplyUpvote

Thank you for your training
Does this sensor show up to 98%?

0

sivaramteerth (https://www.instructables.com/member/sivaramteerth/)

sivaramteerth (https://www.instructables.com/member/sivaramteerth/)

Question 1 year ago

AnswerUpvote

What is the accuracy limit of the oxygen sensor used in this analyzer?
Can it detect the oxygen within a limit of 0.1 - 0.5%?

0

CrumpittRN (https://www.instructables.com/member/CrumpittRN/)

CrumpittRN (https://www.instructables.com/member/CrumpittRN/)

Question 1 year ago on Introduction (https://www.instructables.com/Easy-To-Build-Oxygen-Analyzer-Using-An-Arduino-Com/#intro)

AnswerUpvote

Hi, could this be turned in to a trimix analyzer? Used to Show both 02 and He maybe even the MOD of the mix?
Thanks

0

TiếnB1 (https://www.instructables.com/member/Ti%25E1%25BA%25BFnB1/)

TiếnB1 (https://www.instructables.com/member/Ti%25E1%25BA%25BFnB1/)

4 years ago

ReplyUpvote

Hi, Can it measure the oxygen in the air like in the room???

I want to buid it to measure the oxygen in the factory...

1 reply

0

viola2572 (https://www.instructables.com/member/viola2572/)

viola2572 (https://www.instructables.com/member/viola2572/)TiếnB1

Reply 2 years ago

ReplyUpvote

yes it can

0

VeetuM (https://www.instructables.com/member/VeetuM/)

VeetuM (https://www.instructables.com/member/VeetuM/)

Question 3 years ago on Introduction (https://www.instructables.com/Easy-To-Build-Oxygen-Analyzer-Using-An-Arduino-Com/#intro)

AnswerUpvote

Hi.

i wanted to findout if you had a circuit diagram of the oxygen anlyser you worked On ,i really wanted to see the arrangements.

THANKS!

0

GBhargavi (https://www.instructables.com/member/GBhargavi/)

GBhargavi (https://www.instructables.com/member/GBhargavi/)

3 years ago

ReplyUpvote

Can O2 sensor measures the oxygen in air?
Actually,I want to use this sensor to measure the oxygen in hill areas.is this possible or not?

0

um96 (https://www.instructables.com/member/um96/)

um96 (https://www.instructables.com/member/um96/)

3 years ago

ReplyUpvote

mine is not working i have used an arduino uno and my sensor is envitech oom 102-1 but the display just gives the output calibrating nothing else .

please help me

0

HaliffR (https://www.instructables.com/member/HaliffR/)

HaliffR (https://www.instructables.com/member/HaliffR/)

3 years ago

ReplyUpvote

i want to connect this to piezoelectric valve. the purpose is to keep oxygen at 5% in a small space close environment of biological organism. is it just simple modification of your code? Can someone point me the right direction? thanks!

0

CJR8 (https://www.instructables.com/member/CJR8/)

CJR8 (https://www.instructables.com/member/CJR8/)

4 years ago

ReplyUpvote

Hi! Does this reads water oxygen level?

2 replies

0

akurk (https://www.instructables.com/member/akurk/)

akurk (https://www.instructables.com/member/akurk/)CJR8

Reply 4 years ago

ReplyUpvote

No it does not, it is a gas analyzer. I am not even sure if there is a probe or sensor that reads dissolved O2 in a liquid .

0

ptschram (https://www.instructables.com/member/ptschram/)

ptschram (https://www.instructables.com/member/ptschram/)akurk

Reply 4 years ago

ReplyUpvote

Dissolved oxygen is one of the most common wastewater analyses conducted. Multiple vendors provide ion-specific electrodes

0

SergeyF14 (https://www.instructables.com/member/SergeyF14/)

SergeyF14 (https://www.instructables.com/member/SergeyF14/)

4 years ago

ReplyUpvote

Hi and thanks for replying.
Finally got time to play with it again and do some debugging.
I was using ADS1115 board and at gain 16 it must have been too sensitive or something. Did a coversion of the reading to real mV on the screen and once set to gain 4 I finally get readings that are similar to the multimeter.
Thanks again for the great post!

0

SergeyF14 (https://www.instructables.com/member/SergeyF14/)

SergeyF14 (https://www.instructables.com/member/SergeyF14/)

4 years ago

ReplyUpvote

Hello. Have you tested the readings against some reference oxygen meter?

I have some issues with results - I do get the output, put the readings are dependent on the air pressure to the sensor.

My simple reference is just a multimeter. For my sensor it reads 10.1mV in air.

I am actually testing for nitrogen, so expecting to see a drop. With
nitrogen mix of about 10% O2, on the multimeter I get about 5mV. But on
the arduino the readings translate to like 8%.

I also tried O2 at
high % (did not do reference read on the multimeter, so do not know
what it was) - the readings on the arduino changed into negatives =(

Also, after calibrating to 20.9% O2, if I unplug the sensor it still reads around 1.5% on the arduino.

What am I doing wrong?

1 reply

0

akurk (https://www.instructables.com/member/akurk/)

akurk (https://www.instructables.com/member/akurk/)SergeyF14

Reply 4 years ago

ReplyUpvote

I have tried it with the sensor mentioned in the build. I had an oxycheck o2 analyzer with the same sensor. I had a period of time where I was using nitrox almost every weekend. I have tested it against other analyzers and it was well within 1% which is the acceptable

I build it to calibrate against compressed air 20.9% O2. You need to calibrate as the voltage your sensor output changes with the age of the sensor and the temperature the sensor is in.

Q did you alter the code?
Q did you use the same components
Q Is your sensor within factory spec outputs. I have had bad sensors before.

If you can send me diagram or pic of your build I can look it over. My email is akurk@4divers.ca.

More CommentsPost Comment

Open Menu

  - circuits (https://www.instructables.com/circuits/)
  - workshop (https://www.instructables.com/workshop/)
  - craft (https://www.instructables.com/craft/)
  - cooking (https://www.instructables.com/cooking/)
  - living (https://www.instructables.com/living/)
  - outside (https://www.instructables.com/outside/)
- Log InSignup
- Search (https://www.instructables.com/howto/)
- Following (https://www.instructables.com/feed/)
- Projects (https://www.instructables.com/Easy-To-Build-Oxygen-Analyzer-Using-An-Arduino-Com/#)
  - back (https://www.instructables.com/Easy-To-Build-Oxygen-Analyzer-Using-An-Arduino-Com/#)
  - All Projects (https://www.instructables.com/projects/)
  - Circuits (https://www.instructables.com/Easy-To-Build-Oxygen-Analyzer-Using-An-Arduino-Com/#)
    - back (https://www.instructables.com/Easy-To-Build-Oxygen-Analyzer-Using-An-Arduino-Com/#)
    - All (https://www.instructables.com/circuits/projects/)
    - Apple (https://www.instructables.com/circuits/apple/projects/)
    - Arduino (https://www.instructables.com/circuits/arduino/projects/)
    - Art (https://www.instructables.com/circuits/art/projects/)
    - Assistive Tech (https://www.instructables.com/circuits/assistive-tech/projects/)
    - Audio (https://www.instructables.com/circuits/audio/projects/)
    - Cameras (https://www.instructables.com/circuits/cameras/projects/)
    - Clocks (https://www.instructables.com/circuits/clocks/projects/)
    - Computers (https://www.instructables.com/circuits/computers/projects/)
    - Electronics (https://www.instructables.com/circuits/electronics/projects/)
    - Gadgets (https://www.instructables.com/circuits/gadgets/projects/)
    - Lasers (https://www.instructables.com/circuits/lasers/projects/)
    - LEDs (https://www.instructables.com/circuits/leds/projects/)
    - Linux (https://www.instructables.com/circuits/linux/projects/)
    - Microcontrollers (https://www.instructables.com/circuits/microcontrollers/projects/)
    - Microsoft (https://www.instructables.com/circuits/microsoft/projects/)
    - Mobile (https://www.instructables.com/circuits/mobile/projects/)
    - Raspberry Pi (https://www.instructables.com/circuits/raspberry-pi/projects/)
    - Remote Control (https://www.instructables.com/circuits/remote-control/projects/)
    - Reuse (https://www.instructables.com/circuits/reuse/projects/)
    - Robots (https://www.instructables.com/circuits/robots/projects/)
    - Sensors (https://www.instructables.com/circuits/sensors/projects/)
    - Software (https://www.instructables.com/circuits/software/projects/)
    - Soldering (https://www.instructables.com/circuits/soldering/projects/)
    - Speakers (https://www.instructables.com/circuits/speakers/projects/)
    - Tools (https://www.instructables.com/circuits/tools/projects/)
    - USB (https://www.instructables.com/circuits/usb/projects/)
    - Wearables (https://www.instructables.com/circuits/wearables/projects/)
    - Websites (https://www.instructables.com/circuits/websites/projects/)
    - Wireless (https://www.instructables.com/circuits/wireless/projects/)
  - Workshop (https://www.instructables.com/Easy-To-Build-Oxygen-Analyzer-Using-An-Arduino-Com/#)
    - back (https://www.instructables.com/Easy-To-Build-Oxygen-Analyzer-Using-An-Arduino-Com/#)
    - All (https://www.instructables.com/workshop/projects/)
    - 3D Printing (https://www.instructables.com/workshop/3d-printing/projects/)
    - Cars (https://www.instructables.com/workshop/cars/projects/)
    - CNC (https://www.instructables.com/workshop/cnc/projects/)
    - Electric Vehicles (https://www.instructables.com/workshop/electric-vehicles/projects/)
    - Energy (https://www.instructables.com/workshop/energy/projects/)
    - Furniture (https://www.instructables.com/workshop/furniture/projects/)
    - Home Improvement (https://www.instructables.com/workshop/home-improvement/projects/)
    - Home Theater (https://www.instructables.com/workshop/home-theater/projects/)
    - Hydroponics (https://www.instructables.com/workshop/hydroponics/projects/)
    - Knives (https://www.instructables.com/workshop/knives/projects/)
    - Laser Cutting (https://www.instructables.com/workshop/laser-cutting/projects/)
    - Lighting (https://www.instructables.com/workshop/lighting/projects/)
    - Metalworking (https://www.instructables.com/workshop/metalworking/projects/)
    - Molds & Casting (https://www.instructables.com/workshop/molds-and-casting/projects/)
    - Motorcycles (https://www.instructables.com/workshop/motorcycles/projects/)
    - Organizing (https://www.instructables.com/workshop/organizing/projects/)
    - Pallets (https://www.instructables.com/workshop/pallets/projects/)
    - Repair (https://www.instructables.com/workshop/repair/projects/)
    - Science (https://www.instructables.com/workshop/science/projects/)
    - Shelves (https://www.instructables.com/workshop/shelves/projects/)
    - Solar (https://www.instructables.com/workshop/solar/projects/)
    - Tools (https://www.instructables.com/workshop/tools/projects/)
    - Woodworking (https://www.instructables.com/workshop/woodworking/projects/)
    - Workbenches (https://www.instructables.com/workshop/workbenches/projects/)
  - Craft (https://www.instructables.com/Easy-To-Build-Oxygen-Analyzer-Using-An-Arduino-Com/#)
    - back (https://www.instructables.com/Easy-To-Build-Oxygen-Analyzer-Using-An-Arduino-Com/#)
    - All (https://www.instructables.com/craft/projects/)
    - Art (https://www.instructables.com/craft/art/projects/)
    - Books & Journals (https://www.instructables.com/craft/books-and-journals/projects/)
    - Cardboard (https://www.instructables.com/craft/cardboard/projects/)
    - Cards (https://www.instructables.com/craft/cards/projects/)
    - Clay (https://www.instructables.com/craft/clay/projects/)
    - Costumes & Cosplay (https://www.instructables.com/craft/costumes-and-cosplay/projects/)
    - Digital Graphics (https://www.instructables.com/craft/digital-graphics/projects/)
    - Duct Tape (https://www.instructables.com/craft/duct-tape/projects/)
    - Embroidery (https://www.instructables.com/craft/embroidery/projects/)
    - Fashion (https://www.instructables.com/craft/fashion/projects/)
    - Felt (https://www.instructables.com/craft/felt/projects/)
    - Fiber Arts (https://www.instructables.com/craft/fiber-arts/projects/)
    - Gift Wrapping (https://www.instructables.com/craft/gift-wrapping/projects/)
    - Jewelry (https://www.instructables.com/craft/jewelry/projects/)
    - Knitting & Crochet (https://www.instructables.com/craft/knitting-and-crochet/projects/)
    - Leather (https://www.instructables.com/craft/leather/projects/)
    - Mason Jars (https://www.instructables.com/craft/mason-jars/projects/)
    - No-Sew (https://www.instructables.com/craft/no-sew/projects/)
    - Paper (https://www.instructables.com/craft/paper/projects/)
    - Parties & Weddings (https://www.instructables.com/craft/parties-and-weddings/projects/)
    - Photography (https://www.instructables.com/craft/photography/projects/)
    - Printmaking (https://www.instructables.com/craft/printmaking/projects/)
    - Reuse (https://www.instructables.com/craft/reuse/projects/)
    - Sewing (https://www.instructables.com/craft/sewing/projects/)
    - Soapmaking (https://www.instructables.com/craft/soapmaking/projects/)
    - Wallets (https://www.instructables.com/craft/wallets/projects/)
  - Cooking (https://www.instructables.com/Easy-To-Build-Oxygen-Analyzer-Using-An-Arduino-Com/#)
    - back (https://www.instructables.com/Easy-To-Build-Oxygen-Analyzer-Using-An-Arduino-Com/#)
    - All (https://www.instructables.com/cooking/projects/)
    - Bacon (https://www.instructables.com/cooking/bacon/projects/)
    - BBQ & Grilling (https://www.instructables.com/cooking/bbq-and-grilling/projects/)
    - Beverages (https://www.instructables.com/cooking/beverages/projects/)
    - Bread (https://www.instructables.com/cooking/bread/projects/)
    - Breakfast (https://www.instructables.com/cooking/breakfast/projects/)
    - Cake (https://www.instructables.com/cooking/cake/projects/)
    - Candy (https://www.instructables.com/cooking/candy/projects/)
    - Canning & Preserving (https://www.instructables.com/cooking/canning-and-preserving/projects/)
    - Cocktails & Mocktails (https://www.instructables.com/cooking/cocktails-and-mocktails/projects/)
    - Coffee (https://www.instructables.com/cooking/coffee/projects/)
    - Cookies (https://www.instructables.com/cooking/cookies/projects/)
    - Cupcakes (https://www.instructables.com/cooking/cupcakes/projects/)
    - Dessert (https://www.instructables.com/cooking/dessert/projects/)
    - Homebrew (https://www.instructables.com/cooking/homebrew/projects/)
    - Main Course (https://www.instructables.com/cooking/main-course/projects/)
    - Pasta (https://www.instructables.com/cooking/pasta/projects/)
    - Pie (https://www.instructables.com/cooking/pie/projects/)
    - Pizza (https://www.instructables.com/cooking/pizza/projects/)
    - Salad (https://www.instructables.com/cooking/salad/projects/)
    - Sandwiches (https://www.instructables.com/cooking/sandwiches/projects/)
    - Snacks & Appetizers (https://www.instructables.com/cooking/snacks-and-appetizers/projects/)
    - Soups & Stews (https://www.instructables.com/cooking/soups-and-stews/projects/)
    - Vegetarian & Vegan (https://www.instructables.com/cooking/vegetarian-and-vegan/projects/)
  - Living (https://www.instructables.com/Easy-To-Build-Oxygen-Analyzer-Using-An-Arduino-Com/#)
    - back (https://www.instructables.com/Easy-To-Build-Oxygen-Analyzer-Using-An-Arduino-Com/#)
    - All (https://www.instructables.com/living/projects/)
    - Beauty (https://www.instructables.com/living/beauty/projects/)
    - Christmas (https://www.instructables.com/living/christmas/projects/)
    - Cleaning (https://www.instructables.com/living/cleaning/projects/)
    - Decorating (https://www.instructables.com/living/decorating/projects/)
    - Education (https://www.instructables.com/living/education/projects/)
    - Gardening (https://www.instructables.com/living/gardening/projects/)
    - Halloween (https://www.instructables.com/living/halloween/projects/)
    - Health (https://www.instructables.com/living/health/projects/)
    - Hiding Places (https://www.instructables.com/living/hiding-places/projects/)
    - Holidays (https://www.instructables.com/living/holidays/projects/)
    - Homesteading (https://www.instructables.com/living/homesteading/projects/)
    - Kids (https://www.instructables.com/living/kids/projects/)
    - Kitchen (https://www.instructables.com/living/kitchen/projects/)
    - LEGO & K'NEX (https://www.instructables.com/living/lego-and-knex/projects/)
    - Life Hacks (https://www.instructables.com/living/life-hacks/projects/)
    - Music (https://www.instructables.com/living/music/projects/)
    - Office Supply Hacks (https://www.instructables.com/living/office-supply-hacks/projects/)
    - Organizing (https://www.instructables.com/living/organizing/projects/)
    - Pest Control (https://www.instructables.com/living/pest-control/projects/)
    - Pets (https://www.instructables.com/living/pets/projects/)
    - Pranks, Tricks, & Humor (https://www.instructables.com/living/pranks-tricks-and-humor/projects/)
    - Relationships (https://www.instructables.com/living/relationships/projects/)
    - Toys & Games (https://www.instructables.com/living/toys-and-games/projects/)
    - Travel (https://www.instructables.com/living/travel/projects/)
    - Video Games (https://www.instructables.com/living/video-games/projects/)
  - Outside (https://www.instructables.com/Easy-To-Build-Oxygen-Analyzer-Using-An-Arduino-Com/#)
    - back (https://www.instructables.com/Easy-To-Build-Oxygen-Analyzer-Using-An-Arduino-Com/#)
    - All (https://www.instructables.com/outside/projects/)
    - Backyard (https://www.instructables.com/outside/backyard/projects/)
    - Beach (https://www.instructables.com/outside/beach/projects/)
    - Bikes (https://www.instructables.com/outside/bikes/projects/)
    - Birding (https://www.instructables.com/outside/birding/projects/)
    - Boats (https://www.instructables.com/outside/boats/projects/)
    - Camping (https://www.instructables.com/outside/camping/projects/)
    - Climbing (https://www.instructables.com/outside/climbing/projects/)
    - Fire (https://www.instructables.com/outside/fire/projects/)
    - Fishing (https://www.instructables.com/outside/fishing/projects/)
    - Hunting (https://www.instructables.com/outside/hunting/projects/)
    - Kites (https://www.instructables.com/outside/kites/projects/)
    - Knots (https://www.instructables.com/outside/knots/projects/)
    - Launchers (https://www.instructables.com/outside/launchers/projects/)
    - Paracord (https://www.instructables.com/outside/paracord/projects/)
    - Rockets (https://www.instructables.com/outside/rockets/projects/)
    - Siege Engines (https://www.instructables.com/outside/siege-engines/projects/)
    - Skateboarding (https://www.instructables.com/outside/skateboarding/projects/)
    - Snow (https://www.instructables.com/outside/snow/projects/)
    - Sports (https://www.instructables.com/outside/sports/projects/)
    - Survival (https://www.instructables.com/outside/survival/projects/)
    - Water (https://www.instructables.com/outside/water/projects/)
  - Teachers (https://www.instructables.com/Easy-To-Build-Oxygen-Analyzer-Using-An-Arduino-Com/#)
    - back (https://www.instructables.com/Easy-To-Build-Oxygen-Analyzer-Using-An-Arduino-Com/#)
    - All (https://www.instructables.com/teachers/projects/)
    - ELA (https://www.instructables.com/teachers/projects/?subjects=ela)
    - Math (https://www.instructables.com/teachers/projects/?subjects=math)
    - Micro:bit (https://www.instructables.com/teachers/projects/?subjects=microbit)
    - Science (https://www.instructables.com/teachers/projects/?subjects=science)
    - Social Studies (https://www.instructables.com/teachers/projects/?subjects=social-studies)
    - Engineering (https://www.instructables.com/teachers/projects/?subjects=engineering)
    - Coding (https://www.instructables.com/teachers/projects/?subjects=coding)
    - Electronics (https://www.instructables.com/teachers/projects/?subjects=electronics)
    - Robotics (https://www.instructables.com/teachers/projects/?subjects=robotics)
    - Arduino (https://www.instructables.com/teachers/projects/?subjects=arduino)
    - CNC (https://www.instructables.com/teachers/projects/?subjects=cnc)
    - Laser Cutting (https://www.instructables.com/teachers/projects/?subjects=laser-cutting)
    - 3D Printing (https://www.instructables.com/teachers/projects/?subjects=3d-printing)
    - 3D Design (https://www.instructables.com/teachers/projects/?subjects=3d-design)
    - Art (https://www.instructables.com/teachers/projects/?subjects=art)
    - Music (https://www.instructables.com/teachers/projects/?subjects=music)
    - Theatre (https://www.instructables.com/teachers/projects/?subjects=theatre)
    - Wood Shop (https://www.instructables.com/teachers/projects/?subjects=wood-shop)
    - Metal Shop (https://www.instructables.com/teachers/projects/?subjects=metal-shop)
    - Resources (https://www.instructables.com/teachers/projects/?subjects=resources)
    - Grades K-2 (https://www.instructables.com/teachers/projects/?groups=k-2)
    - Grades 3-5 (https://www.instructables.com/teachers/projects/?groups=3-5)
    - Grades 6-8 (https://www.instructables.com/teachers/projects/?groups=6-8)
    - Grades 9-12 (https://www.instructables.com/teachers/projects/?groups=9-12)
    - University+ (https://www.instructables.com/teachers/projects/?groups=university)
- Contests (https://www.instructables.com/contest/)
- Teachers (https://www.instructables.com/teachers/)
- Publish (https://www.instructables.com/Easy-To-Build-Oxygen-Analyzer-Using-An-Arduino-Com/#)
  - back (https://www.instructables.com/Easy-To-Build-Oxygen-Analyzer-Using-An-Arduino-Com/#)
  - New Instructable (https://www.instructables.com/editInstructable/new/)
  - Drafts (https://www.instructables.com/editInstructable/drafts/)
  - Published (https://www.instructables.com/editInstructable/published/)
  - Why Publish Instructables? (https://www.instructables.com/create/)
  - Writing an Instructable (https://www.instructables.com/class/How-to-Write-an-Instructable-Class/)

Easy to Build Oxygen Analyzer Using an Arduino Compatible Micro Controller by akurk (https://www.instructables.com/member/akurk/)Follow Download Favorite I Made It View Comments (https://www.instructables.com/Easy-To-Build-Oxygen-Analyzer-Using-An-Arduino-Com/#discuss) Share More Options

Facebook Twitter Pinterest Google Classroom

Flag

- Wrong Category
- Inappropriate
- Incomplete
- Spam

Add To Collection Add To Contest Edit

Categories

- Circuits (https://www.instructables.com/circuits/)
- Workshop (https://www.instructables.com/workshop/)
- Craft (https://www.instructables.com/craft/)
- Cooking (https://www.instructables.com/cooking/)
- Living (https://www.instructables.com/living/)
- Outside (https://www.instructables.com/outside/)
- Teachers (https://www.instructables.com/teachers/)

About Us

- Who We Are (https://www.instructables.com/about/)
- Why Publish? (https://www.instructables.com/create/)
- Jobs (https://www.instructables.com/jobs/)

Resources

- Sitemap (https://www.instructables.com/sitemap/)
- Help (https://www.instructables.com/how-to-write-a-great-instructable/)
- Contact (https://www.instructables.com/contact/)

Find Us

- (https://www.instagram.com/instructables/)
- (https://www.pinterest.com/instructables)
- (https://www.facebook.com/instructables)
- (https://www.twitter.com/instructables)

© 2021 Autodesk, Inc.

- Terms of Service (http://usa.autodesk.com/adsk/servlet/item?siteID=123112&id=21959721)|
- Privacy Statement (http://usa.autodesk.com/adsk/servlet/item?siteID=123112&id=21292079)|
- Privacy settings|
- Legal Notices & Trademarks (http://usa.autodesk.com/legal-notices-trademarks/)

Autodesk (http://www.autodesk.com/)

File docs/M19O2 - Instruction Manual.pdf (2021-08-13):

# Instruction Manual M19O2 Oxygen Concentrator

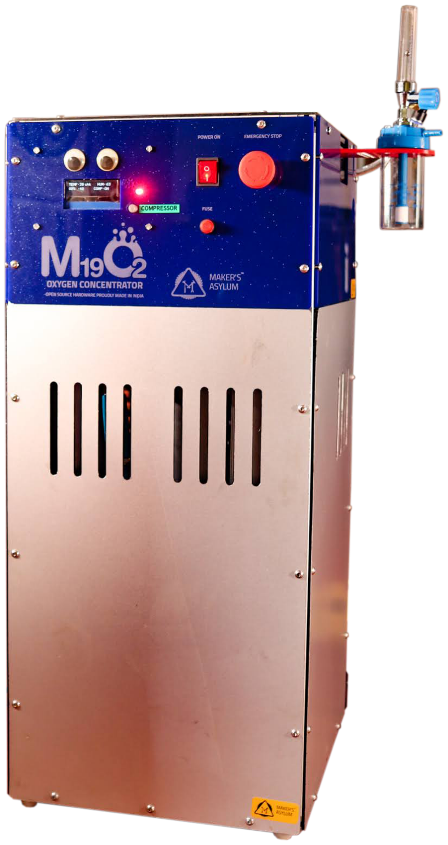
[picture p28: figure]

Maker's Asylum | House Number 661, Mapusa-Moira Rd, Moira, Goa 403507
Release date : 26 Jul 2021 | 1

### INDEX

1. DESCRIPTION
2. SAFETY NOTICES
3. HOW IT WORKS
4. M19O2 PARTS IDENTIFICATION
5. FRONT PANEL
6. SIEVE ASSEMBLY
7. PNEUMATIC SCHEMATIC
8. PNEUMATIC PARTS IDENTIFICATION
9. ELECTRICAL SCHEMATIC
10. ELECTRICAL PARTS IDENTIFICATION
11. INSTALLATION
12. MAINTENANCE
13. TROUBLESHOOTING
14. SPECIFICATIONS
15. DIMENSIONS
16. REPRESENTATION & WARRANTIES
17. FAQ

What is Maker’s Asylum ?

What is M-19 INITIATIVE (MAKERS VS COVID19)?

M-19 Projects

18. CONTACT US
Maker's Asylum | House Number 661, Mapusa-Moira Rd, Moira, Goa 403507

# 1. DESCRIPTION

The M19O2 Oxygen Concentrator is designed to provide over 90% concentrated oxygen between 10 to 15 litres per minute. It uses the Pressure Swing Adsorption (PSA) process to trap and remove Nitrogen from ambient air, thereby allowing enriched Oxygen to be available at the output. It achieves this using Lithium based molecular sieve zeolite. The built in 2.4 hp (1.8 kW) high flow rate, oil free compressor provides sufficient capacity for the desired concentrated Oxygen output. Ambient, dry air has a concentration of 78.08% Nitrogen, 20.95% Oxygen, 0.93% Argon, with the balance consisting mainly of CO2. By capturing this ambient Nitrogen, the concentration of Oxygen can be increased up to a maximum of 95.55% using Lithium based zeolite using the PSA process.

To enable use in high humidity conditions, it incorporates a moisture removal stage with a built-in auto-drain valve. An electro-chemical oxygen sensor is included in line at the output stage to allow continuous monitoring of the concentration. A color coded LED indicator lights red for concentration below 80%, blue for 80% to 90% and green for more than 90% thus visually indicating when it is safe to use the machine even from a distance. The digital display shows oxygen concentration, ambient humidity, ambient temperature, and compressor status (on/off). The compressor can be turned on/off using the push button control on the front panel.

The safety emergency switch can be used at any time to turn off the machine instantly. The front panel also has a 10 Amp fuse (5x20 mm) for protection in case of over current faults. Inside the machine is a pressure overload switch adjusted to switch off the compressor if pressure exceeds a safe limit.

The machine is built on a rigid, aluminum extrusion frame with acrylic and composite aluminum panelling suitable for use in hospital environments. A tilt handle and two caster wheels allow the machine to be tilted and moved around easily. The machine can be powered from a standard, 230 V / 16 A socket outlet.

The M19O2 Oxygen Concentrator is a result of the collaborative effort of the M19 Collective - a collection of makerspaces, community organisations, foundations, industries, universities, researchers and individuals making a collaborative effort to foster open innovation and especially open hardware around the country using decentralised approach and knowledge sharing.

More information about the M19 initiative can be found at this link
https://www.makersasylum.com/m19o2/

Detailed engineering information can be found on our Github repository at this link https://github.com/MakersAsylumIndia/M19O2

For additional information, comments or feedback, please EMail us at
info@makersasylum.com

LICENSES
Hardware | CERN Open Hardware License Version 2 - Strongly Reciprocal (CERN-OHL-S-2.0) (https://spdx.org/licenses/CERN-OHL-S-2.0.html)
Software | MIT open source license (http://opensource.org/licenses/MIT)
Documentation | Creative Commons Attribution 4.0 International License (http://creativecommons.org/licenses/by/4.0/)
Maker's Asylum | House Number 661, Mapusa-Moira Rd, Moira, Goa 403507

# 2. SAFETY NOTICES

☠ ● This unit is not a life-support device , and oxygen therapy could potentially be hazardous for life.

Always follow your health care providers directions and warnings while using this machine.

- Always allow the machine to stabilize to its operating parameters before using it on a patient. It takes between 2 to 5 minutes for the machine to reach its operating parameters.
- The machine requires 230 V, 50Hz single phase supply. Inverter backup power systems sometimes provide non-sinusoidal (stepped wave) outputs. In rare cases, this can affect compressor performance. In such situations, consider changing over to a genset based backup power supply.
- The machine produces high purity Oxygen at high volumes which can be a serious burning hazard. Please install the machine away from sources of open flame, sparks or high heat. Also, when being used in very dry environments that can cause static electricity build up in humans, please use anti-static mats, anti-static grounding straps or similar devices to safely discharge the static energy.
- Never close the output flow control valve completely since it can lead to higher pressure within the pneumatic system of the machine. Never obstruct the output flow.
- Never use any hydrocarbon or petroleum based products near or for cleaning the machine.
- If any of the machine cover panels need to be opened for any reason, please make sure the machine is switched off, and the electrical plug is disconnected from the wall socket outlet.
- Do not allow any liquid to spill over the machine, or use any liquids for cleaning it.
- While the machine incorporates dust filters at the air intake and the oxygen outlets, it is recommended to make sure the operating environment is dust free and as dry and cool as possible.
- Always install the machine on a flat level surface to prevent it from sliding while in use and to prevent tipping over.
- Do not place any items on the top panel of the machine.
- When moving the machine, always use the tilt handle to lean the machine backwards until the two caster wheels engage, and then roll it. Be careful while doing so since the machine is heavy.
- When the machine is in use, do not leave it unattended.
- Ensure that the air intake vents at the back panel of the machine do not have any obstruction or get blocked.
- STORAGE : If the machine is not to be used, please store it in a cool (less than 30 ℃) and low humidity (less than 40 %RH) environment.
Maker's Asylum | House Number 661, Mapusa-Moira Rd, Moira, Goa 403507

# 3. HOW IT WORKS

Ambient Air consists of 78.08% Nitrogen, 20.95% Oxygen, 0.93% Argon, and 0.04% other trace gases, most of which consists of CO2

. The M19O2 Oxygen concentrator, removes Nitrogen from ambient air, resulting in enriched oxygen available at the output using a process called Pressure Swing Adsorption. (https://en.wikipedia.org/wiki/Pressure_swing_adsorption) (PSA).

Pressure Swing Adsorption process for the generation of enriched oxygen gas from ambient air utilises the ability of a synthetic Zeolite Molecular Sieve to adsorb nitrogen. Nitrogen molecules get trapped within the crystalline structure of the Zeolite, while the Oxygen molecules pass through unrestricted.

A PSA concentrator consists of two canisters filled with Zeolite Molecular sieve as adsorbers. Compressed Air passes up through one of the canisters where the molecular sieve selectively adsorbs Nitrogen, allowing the remaining Oxygen to pass on up through the canister to the output. When the first canister gets saturated with Nitrogen, the inlet compressed air is diverted to the second canister. While the second canister is getting pressurised and saturated, the first canister is regenerated by desorbing nitrogen through depressurisation and purging it with some of the oxygen from the second canister. This cycle is repeated, swinging between pressurisation for oxygen production (adsorption), and regeneration by purging/venting for removal of nitrogen (desorption).

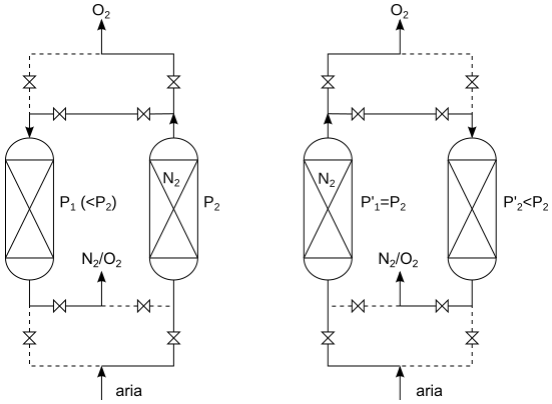
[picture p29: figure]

PSA Process Schematic
Credit
original image: User: Daniele Pugliesi < https://commons.wikimedia.org/wiki/File:Adsorbimento_-_layout_rigenerazione.svg > conversion from JPEG to SVG: User: Personification of plenty, CC BY 3.0 < https://creativecommons.org/licenses/by/3.0 >, via Wikimedia Commons
Maker's Asylum | House Number 661, Mapusa-Moira Rd, Moira, Goa 403507

# 4. M19O2 PARTS IDENTIFICATION

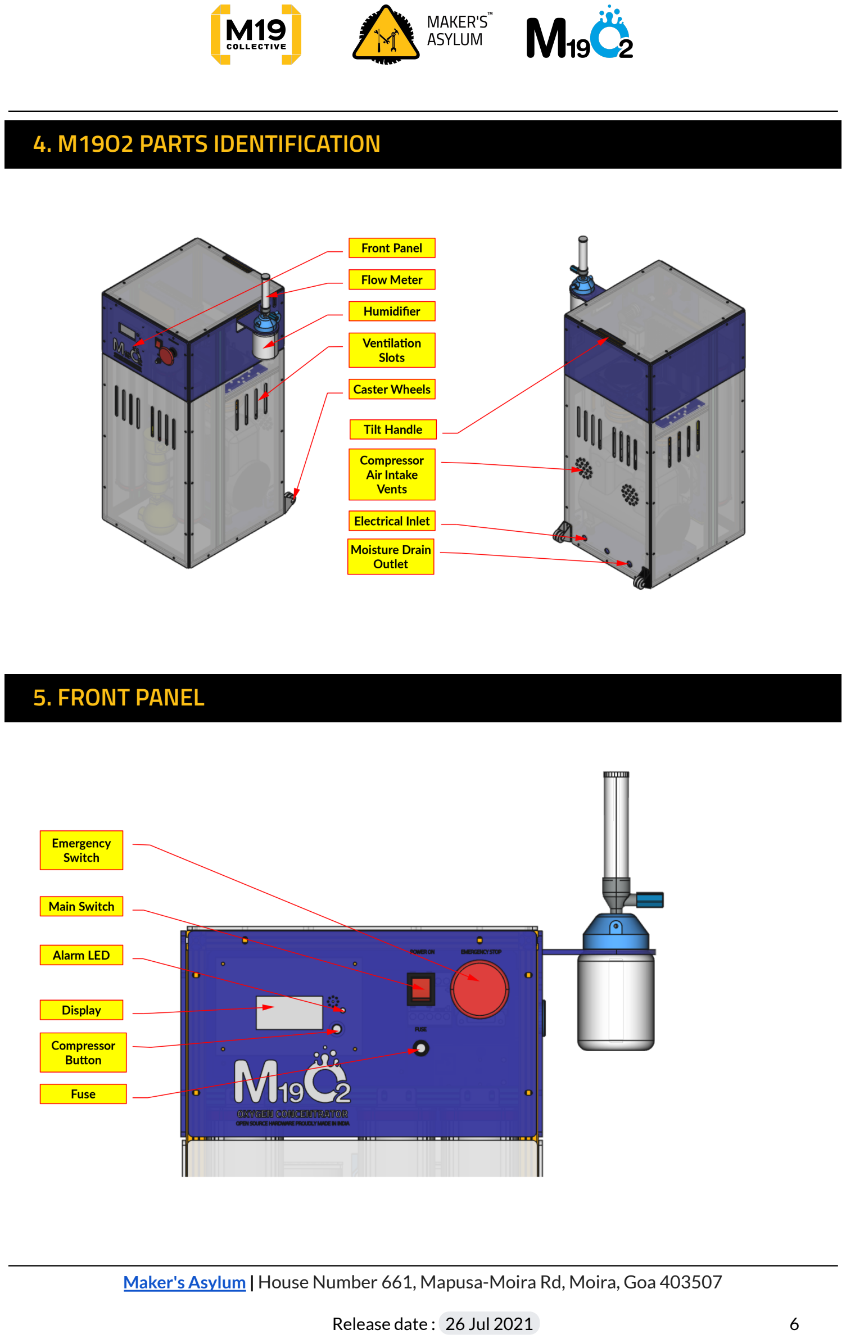
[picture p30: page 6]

# 5. FRONT PANEL

Maker's Asylum | House Number 661, Mapusa-Moira Rd, Moira, Goa 403507

# 6. SIEVE ASSEMBLY

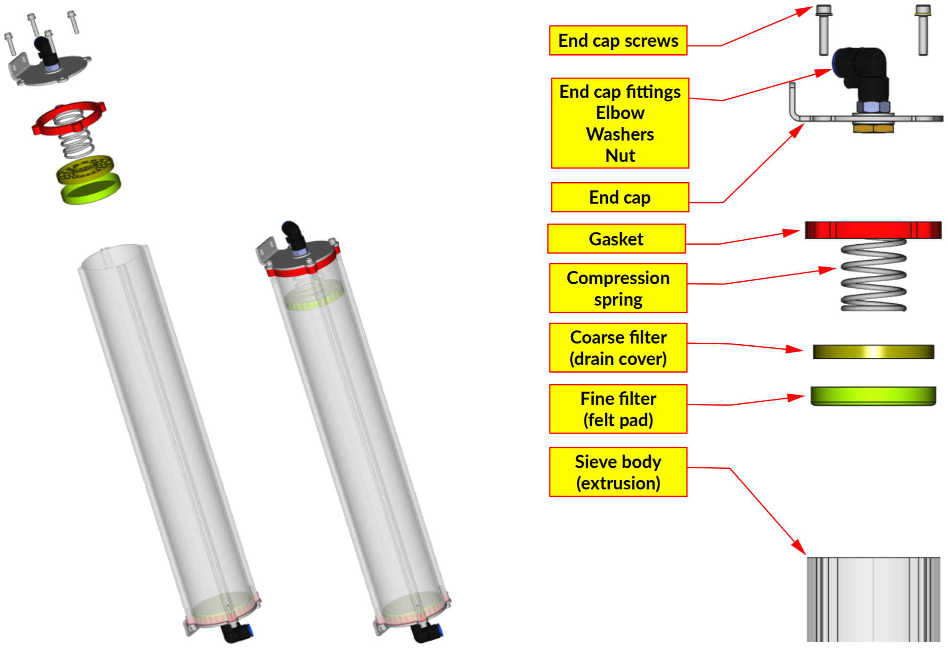
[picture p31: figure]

Maker's Asylum | House Number 661, Mapusa-Moira Rd, Moira, Goa 403507

# 7. PNEUMATIC SCHEMATIC

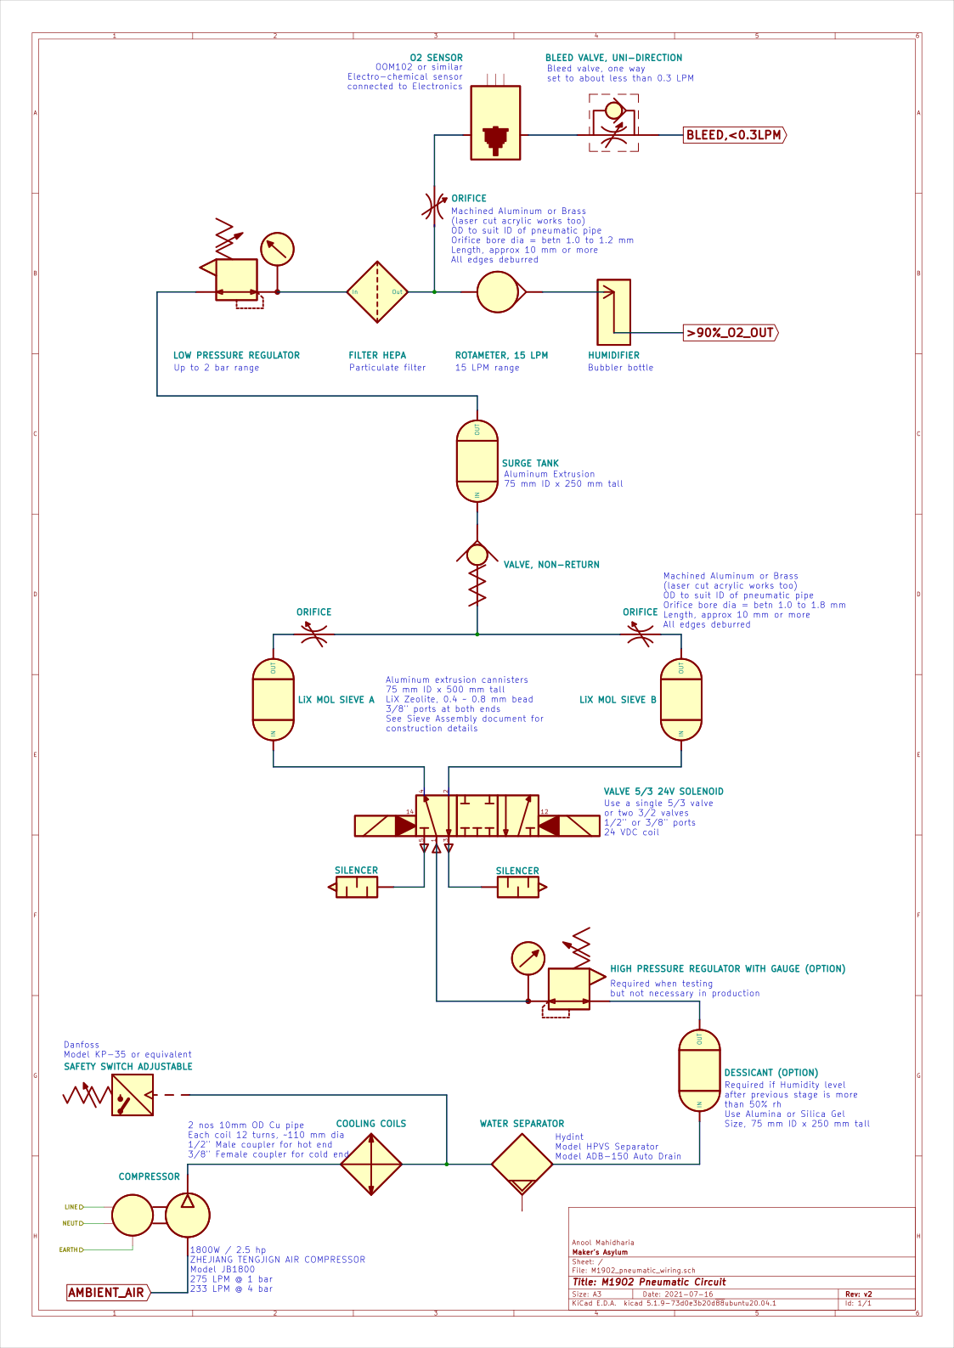
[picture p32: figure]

Maker's Asylum | House Number 661, Mapusa-Moira Rd, Moira, Goa 403507

# 8. PNEUMATIC PARTS IDENTIFICATION

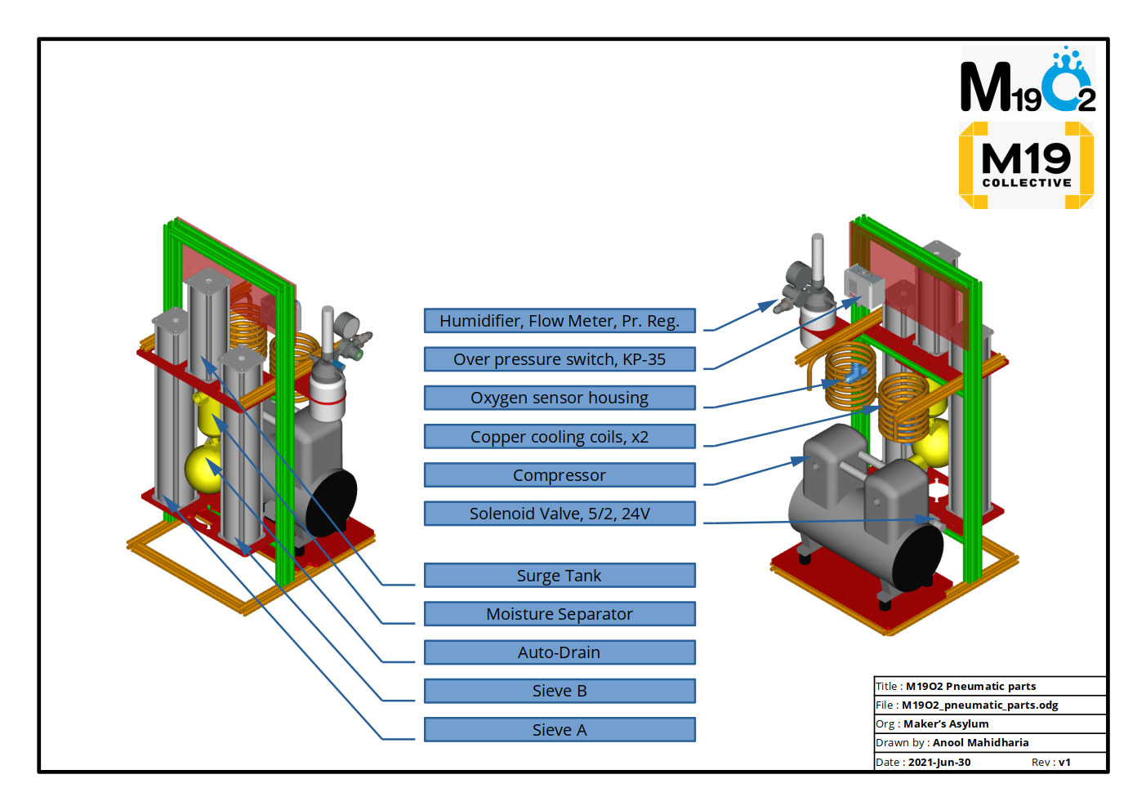
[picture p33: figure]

Maker's Asylum | House Number 661, Mapusa-Moira Rd, Moira, Goa 403507

# 9. ELECTRICAL SCHEMATIC

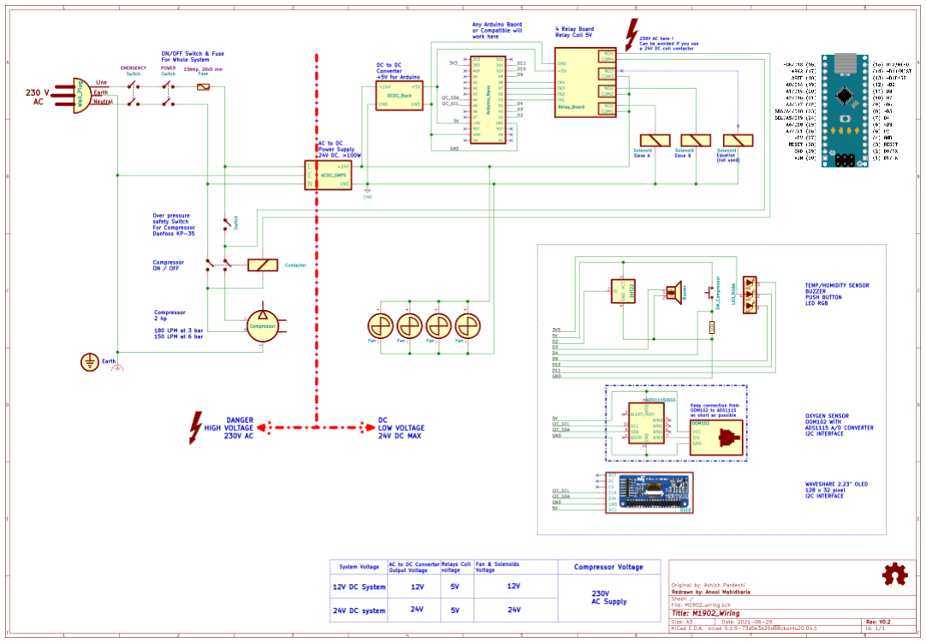
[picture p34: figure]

Maker's Asylum | House Number 661, Mapusa-Moira Rd, Moira, Goa 403507

# 10. ELECTRICAL PARTS IDENTIFICATION

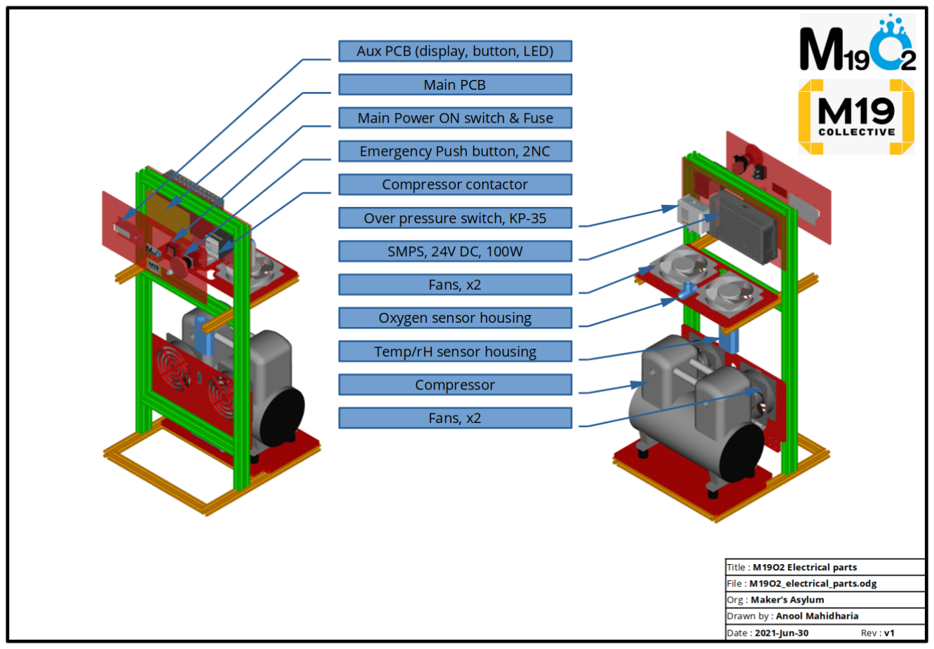
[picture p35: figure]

Maker's Asylum | House Number 661, Mapusa-Moira Rd, Moira, Goa 403507

# 11. INSTALLATION

- Place the machine on a level surface and make sure there are no obstructions on the rear and sides.
- The moisture trap auto-drain outlet is at the back of the machine. At regular intervals, the moisture collected in the separator drains out. Make sure to connect this to a drain.
- The machine requires electrical power from a 230 V AC, 50 Hz, 16 A switched socket outlet. The electrical connection MUST have proper grounding.
- Connect the plug of the machine to the wall socket.
- Turn on the Power Switch on the front panel. If the indicator light does not turn on, make sure the Emergency Switch is disengaged by rotating its knob.
- Check Troubleshooting if the indicator still does not light up.
- In a few seconds, the timing cycle controlled via the embedded microcontroller will start actuating the electrical solenoid coils.
- Make sure the flow control adjustment knob is set to the fully open position.
- Turn on the compressor by pressing the pushbutton on the front panel.
- The PSA process will be initiated, and the flow meter will indicate the output flow in lpm.
- Adjust the flow control adjustment knob for the desired flow rate between 10 to 15 lpm.
- The front panel digital display shows the output oxygen concentration level, ambient temperature, ambient humidity and the status of the compressor.
- It can take between 2 to 5 minutes for the oxygen concentration level to reach >90%. Below 80% concentration, the LED on the front panel lights up Red, for 80% to 90% concentration, it lights up Blue, and once the concentration exceeds 90%, it lights green.
- At this point, it is safe to connect the output of the machine as desired.
- To stop the machine, first turn off the compressor using the pushbutton on the front panel, and wait for a few minutes to allow the fans to cool down the compressor, the pressure inside the system to dissipate, and for the oxygen sensor value to reach back to ambient value of approximately 21%. After that, the main switch can be turned off.
Maker's Asylum | House Number 661, Mapusa-Moira Rd, Moira, Goa 403507

# 12. MAINTENANCE

- Clean the outside of the oxygen concentrator
- Begin by unplugging the oxygen concentrator from its power source
- Dip a soft cloth in a solution of mild dishwashing soap and warm water
- Squeeze cloth until damp and wipe down the concentrator
- Rinse cloth clean and remove any excess soap on concentrator
- Let concentrator air-dry or dry with a lint-free cloth
- Change the particle filter
- Replacing the HEPA air filter inside the machine is recommended once a year. If the machine is used for long durations, then replacement is recommended at shorter intervals.
- A set of allen keys will be required for this operation.
- Begin by removing the acrylic panel on the left side of the machine near the humidifier / flowmeter.
- Remove the HEPA filter connected just before the flow meter. Detaching the two tubes connected to the HEPA filter may take some effort.
- Replace the HEPA filter with a fresh one. Contact the manufacturer for replacement filters.
- Destroy and discard the old, used filter.
- Replace the side acrylic panel.
- Additional tips
- Avoid using an oxygen concentrator in a dusty environment
- Use a voltage stabilizer to offset voltage fluctuation (see Safety Notice for additional information)
- Rest the concentrator for 20 – 30 minutes after continuous usage for 4 -- 6 hours
- Do not submerge the concentrator in water
- Cleaning the outside of the concentrator is recommended on a weekly basis.
- Recommended service intervals for the concentrator should be at least once annually, or more depending on usage time.
- Place the concentrator at least 300 to 600 mm (1 to 2 feet) away from surrounding walls.
Maker's Asylum | House Number 661, Mapusa-Moira Rd, Moira, Goa 403507

# 13. TROUBLESHOOTING

ISSUE | POSSIBLE CAUSE | WHAT TO DO
No display and no indicators light up when machine is connected to electrical outlet | No power to the concentrator | Disconnect plug from electrical socket. Check electrical socket for presence of 230 V AC. If the fuse is blown or MCB has tripped, contact the manufacturer. Check the condition of the plug for broken or disconnected wires. Check and replace the fuse on the front panel. Fuse rating is 10A slo-blo or time delay type, 20x5 mm glass cartridge. If the fuse blows repeatedly, contact the manufacturer. Make sure the outlet and switch are rated for 16 Amps. Rotate and release the EMERGENCY button. If problem continues, contact the manufacturer.
No oxygen flow (Put the end of the cannula in a cup of water to make sure there is no flow; a steady flow of bubbles should be seen when oxygen flow is present) | Tubing is disconnected or kinked | Reconnect, straighten, or replace tubing.
| Flow rate not set properly | Check the flow meter on the concentrator unit – make sure that flow rate is set to your prescription level.
| Humidifier cross-threaded | Disconnect humidifier from concentrator outlet, and reconnect without cross-threading.
| Concentrator power is off | Turn concentrator power switch to ON position.
| Machine malfunction | Switch to your back-up system and contact the manufacturer.
Flowmeter won’t adjust | Tubing is disconnected or kinked | Reconnect, straighten, or replace tubing.
Machine turns off by itself | Machine malfunction | Switch to your back-up system and contact the manufacturer.
RED or BLUE LED indicator lights up on front panel | RED = Oxygen concentration is below 80% BLUE = Oxygen concentration is between 80% to 90% | It takes about 2 --3 minutes for the machine to reach >90% concentration levels. If the concentration level does not increase, contact the manufacturer.
Water in supply tubing | Some condensation is normal, but may block flow of oxygen | If necessary, replace the supply tubing. Try using less water in the humidifier. Keep tubing elevated off the floor.
Maker's Asylum | House Number 661, Mapusa-Moira Rd, Moira, Goa 403507

# 14. SPECIFICATIONS

- O2 concentration | >92 %,

-2
/+3 %
- Output flow rate | up to 15 lpm
- Altitude limits | -10 % reduction in output flow at 1000 m elevation gain
- Electrical Input | 230 V AC, 50 Hz, 10 Amps, single phase, 2000 VA
- Ambient Temperature | 20 ℃ to 35 ℃
- Ambient Humidity | 0 %RH to 70 %RH
- Noise Emission | < 75 dB(A)
- Dimensions | 820 H x 410 D x 370 W, in mm
(excluding caster wheels, tilt handle, external flow meter/humidifier)
- Weight | 30 kgs, approx
- Safety Features
- Emergency Switch
- Fuse, overcurrent protection (5x20 mm, glass cartridge,slo-blo)
- Visual Indicator for concentration level
■ <80% | = Red
■ >80%, <90% | = Blue
■ >90% | = Green
- Over pressure cutoff (set to trip at 5 bar, reset at 1 bar)
Maker's Asylum | House Number 661, Mapusa-Moira Rd, Moira, Goa 403507

# 15. DIMENSIONS

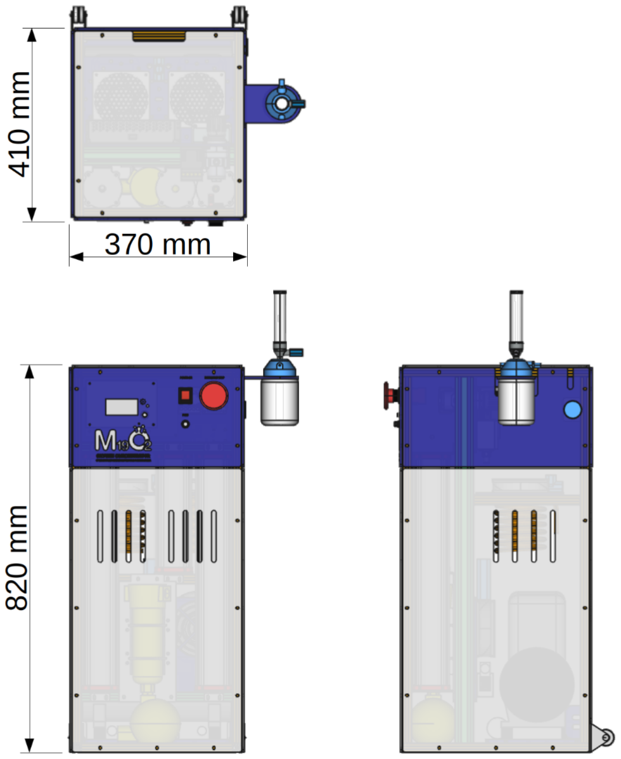
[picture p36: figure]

Maker's Asylum | House Number 661, Mapusa-Moira Rd, Moira, Goa 403507

# 16. REPRESENTATION & WARRANTIES

M19O2 is intended for use in COVID-19 like situations only. All reasonable care, prevention and precautions (including sanitisation) have been taken while designing and manufacturing M19O2.

M19O2 is suitable for usage in (inter-alia) only for the following:

Healthcare personnel refers to all paid and unpaid persons serving in healthcare settings who have the potential for direct or indirect exposure to patients or infectious materials, including body substances (e.g., blood, tissue, and specific body fluids); contaminated medical supplies, devices, and equipment; contaminated environmental surfaces; or contaminated air. These healthcare personnel include, but are not limited to, emergency medical service personnel, nurses, nursing assistants, physicians, technicians, therapists, phlebotomists, pharmacists, dentists and dental hygienists, students and trainees, contractual staff not employed by the healthcare facility, and persons not directly involved in patient care, but who could be exposed to infectious agents that can be transmitted in the healthcare setting (e.g., clerical, dietary, environmental services, laundry, security, engineering and facilities management, administrative, billing, and volunteer personnel.

Maker’s Asylum (or any of its representatives) makes no warranties, expressed or implied, including, but not limited to, any implied warranty of fitness of M19O2 except for usage for COVID 19 purposes and in accordance with the prescribed standards.

Users shall be solely responsible for determining whether M19O2 is fit for a particular purpose and suitable for the user's method of use or application.

Maker’s Asylum shall not be responsible for any inappropriate use and/ or misuse of the M19O2 by the user and any resultant effect/ impact/ injury.

Governing law shall be the laws of India and the courts at New Delhi shall have exclusive jurisdiction.

M19O2, the M19O2 logo, are either registered trademarks or trademarks of Asylum Innovation Private Ltd , registered company in India.

Maker's Asylum | House Number 661, Mapusa-Moira Rd, Moira, Goa 403507

# 17. FAQ

## What is Maker’s Asylum ?

Maker’s Asylum is a community space focussed on fostering innovation through hands-on learning. It also provides access to an ecosystem of stakeholders which includes Governments, Businesses, Incubators/Accelerators, Investors and subject matter experts. The space houses various labs that are co-located in order to facilitate prototyping of ideas that are interdisciplinary in nature.

## What is M-19 INITIATIVE (MAKERS VS COVID19) ?

Makerspaces have traditionally been innovation hubs at the time of crisis for communities across the world. The reason - quick access to tools and equipment in order to prototype solutions “rapidly”. Maker’s Asylum is committed to the cause of contributing meaningfully to the COVID19 pandemic! The M-19 Initiative is aimed at bringing together maker spaces, communities, individuals and industry on a common “distributed intelligence” platform to rapidly iterate and devise designs to help fight against coronavirus while also creating a blueprint for a “distributed manufacturing” plan.

The M19 Collective is a collection of makerspaces, community organisations, foundations, industries, universities, researchers and individuals making a collaborative effort to foster open innovation and especially open hardware around the country using decentralised approach and knowledge sharing!

## M-19 Projects

- M-19O2 Oxygen Concentrator (https://www.makersasylum.com/m19o2/)
Activation of local communities to make M19 Oxygen Concentrator (with indigenously sourced parts) in cities, towns and villages in India and building capacity to manufacture & maintain locally and in a decentralised manner.
- M-19 ReBreather (https://shop.makersasylum.com/collections/face-shields/products/m-19-rebreather-mask-with-replaceable-carbon-activated-hepa-filters)
M-19 ReBreather Smart Air Purifier with Replaceable Carbon activated HEPA Filters is an active respirator to help breathing comfortably inside an N-95 mask. Especially designed for senior citizens for comfortable breathing.
- M-19 Face Shields (https://www.makersasylum.com/m19-shields/)
The M-19 initiative started with a thought of giving 1000 M-19 shields to the frontline workers. However, in 49 days we were able to activate 42 cities, towns and villages through our open source design and give over 1 Million M-19 face shields through the M19 Collective.
- M-19 MAPR (https://www.makersasylum.com/m19-mapr/)
A low cost powered-air purifying respirator (PAPR) for use in reducing exposure to airborne particles. This PAPR is designed to provide constant filtered airflow to healthcare workers in high risk environments during the COVID-19 pandemic.

# 18. CONTACT US

Website | : https://www.makersasylum.com/
EMail | : info@makersasylum.com
Phone | : +919004686828
| Maker's Asylum | House Number 661, Mapusa-Moira Rd, Moira, Goa 403507

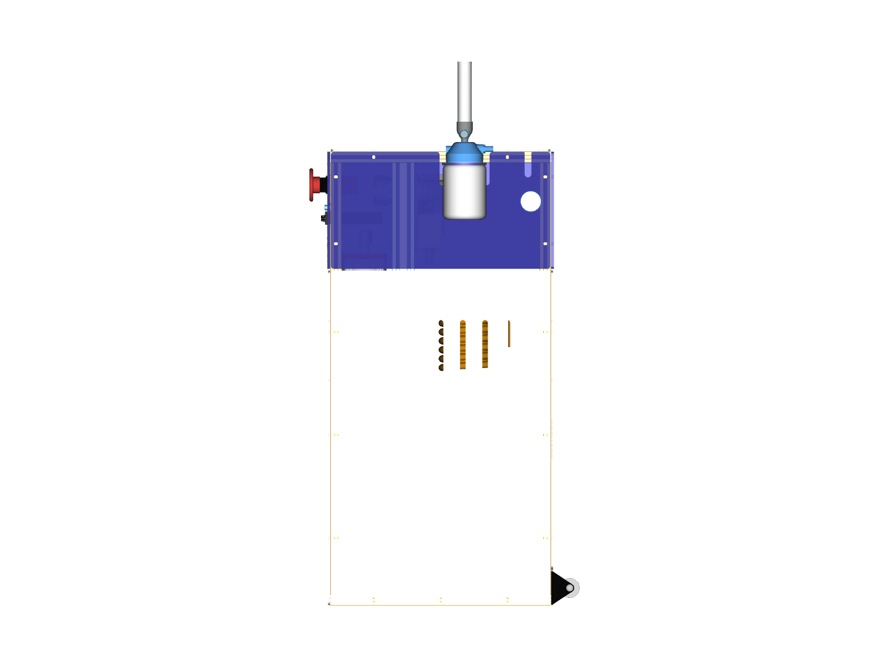
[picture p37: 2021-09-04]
engineering/CAD/M19O2/M19O2_assembly/renders/M19O2_right.png

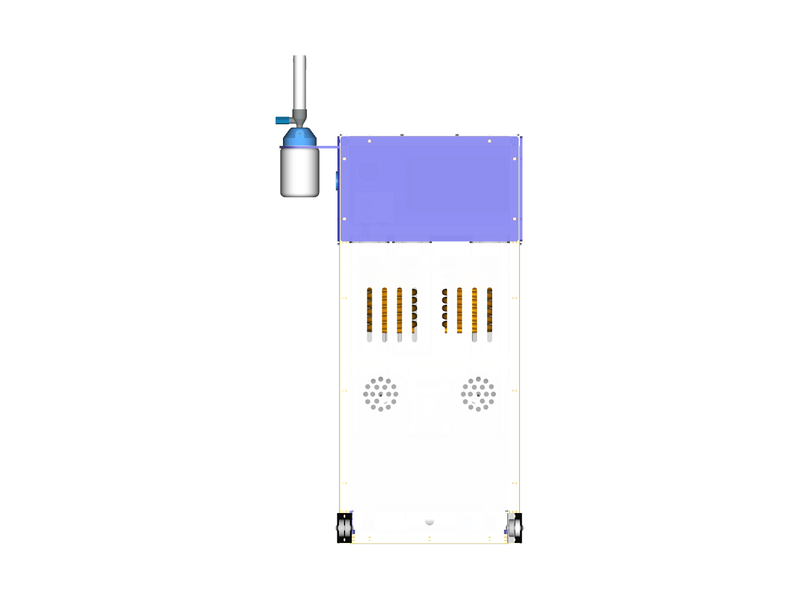
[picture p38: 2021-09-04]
engineering/CAD/M19O2/M19O2_assembly/renders/M19O2_back.png

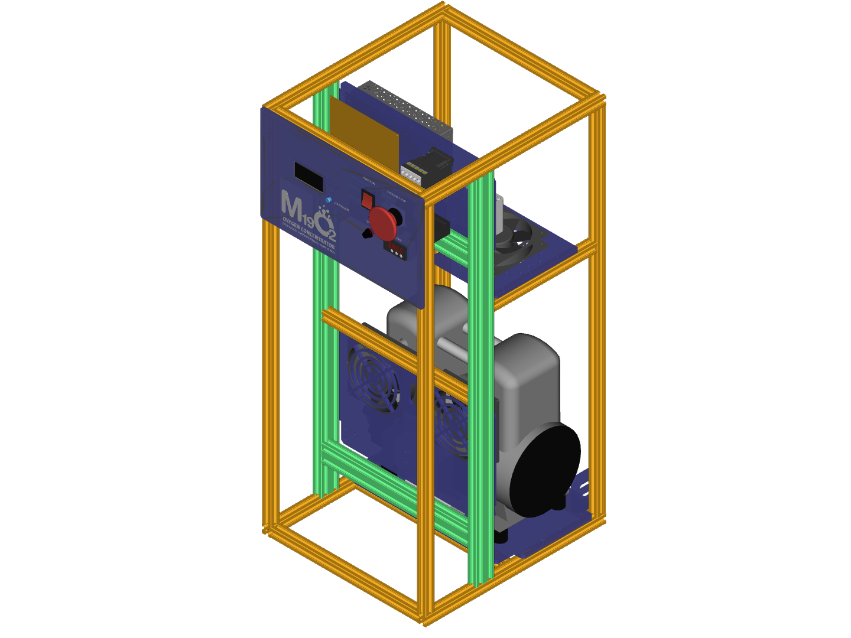
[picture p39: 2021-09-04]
engineering/CAD/M19O2/M19O2_assembly/renders/electrical_frnt.png

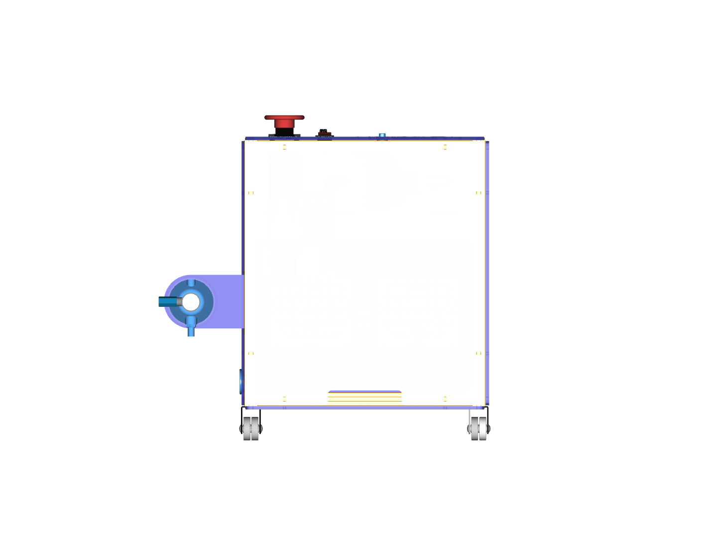
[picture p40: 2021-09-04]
engineering/CAD/M19O2/M19O2_assembly/renders/M19O2_top.png

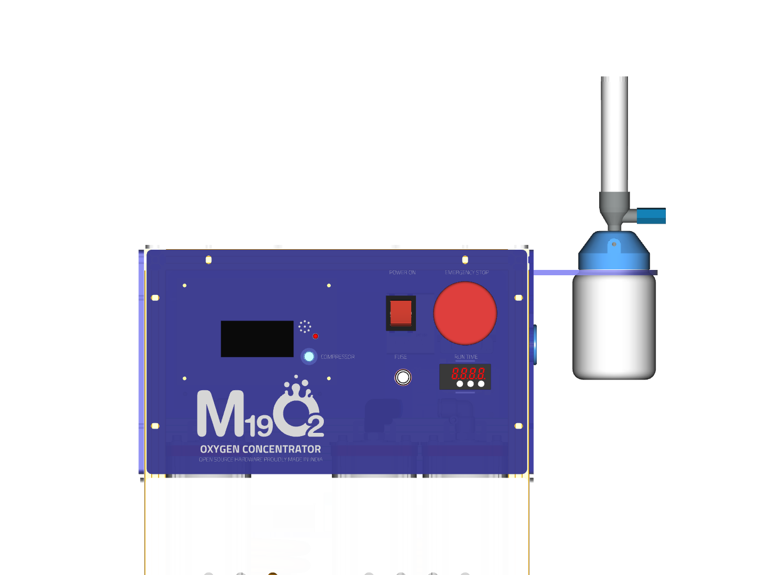
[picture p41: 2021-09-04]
engineering/CAD/M19O2/M19O2_assembly/renders/M19O2_front_panel.png

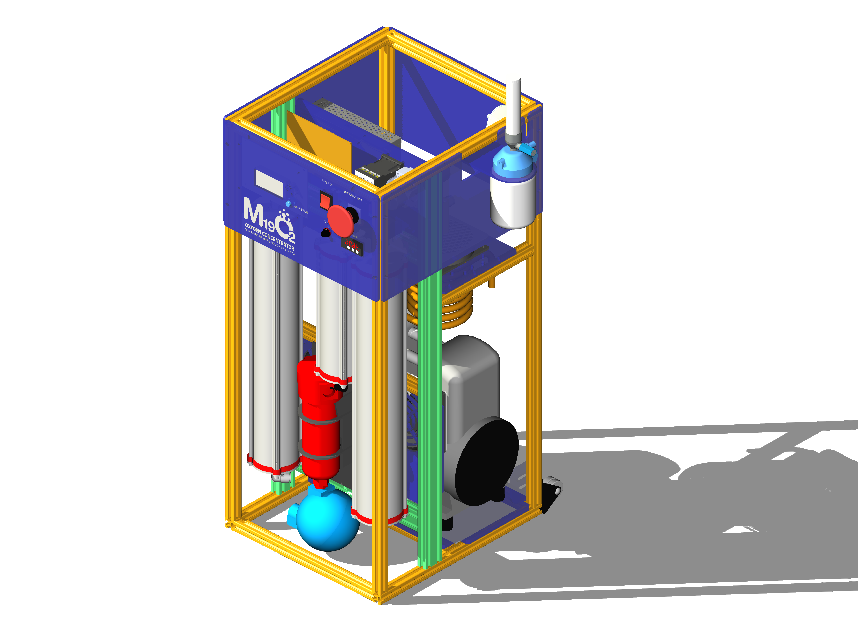
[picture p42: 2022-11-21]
engineering/CAD/M19O2/M19O2_assembly/renders/M19O2_iso_front_HD3.png

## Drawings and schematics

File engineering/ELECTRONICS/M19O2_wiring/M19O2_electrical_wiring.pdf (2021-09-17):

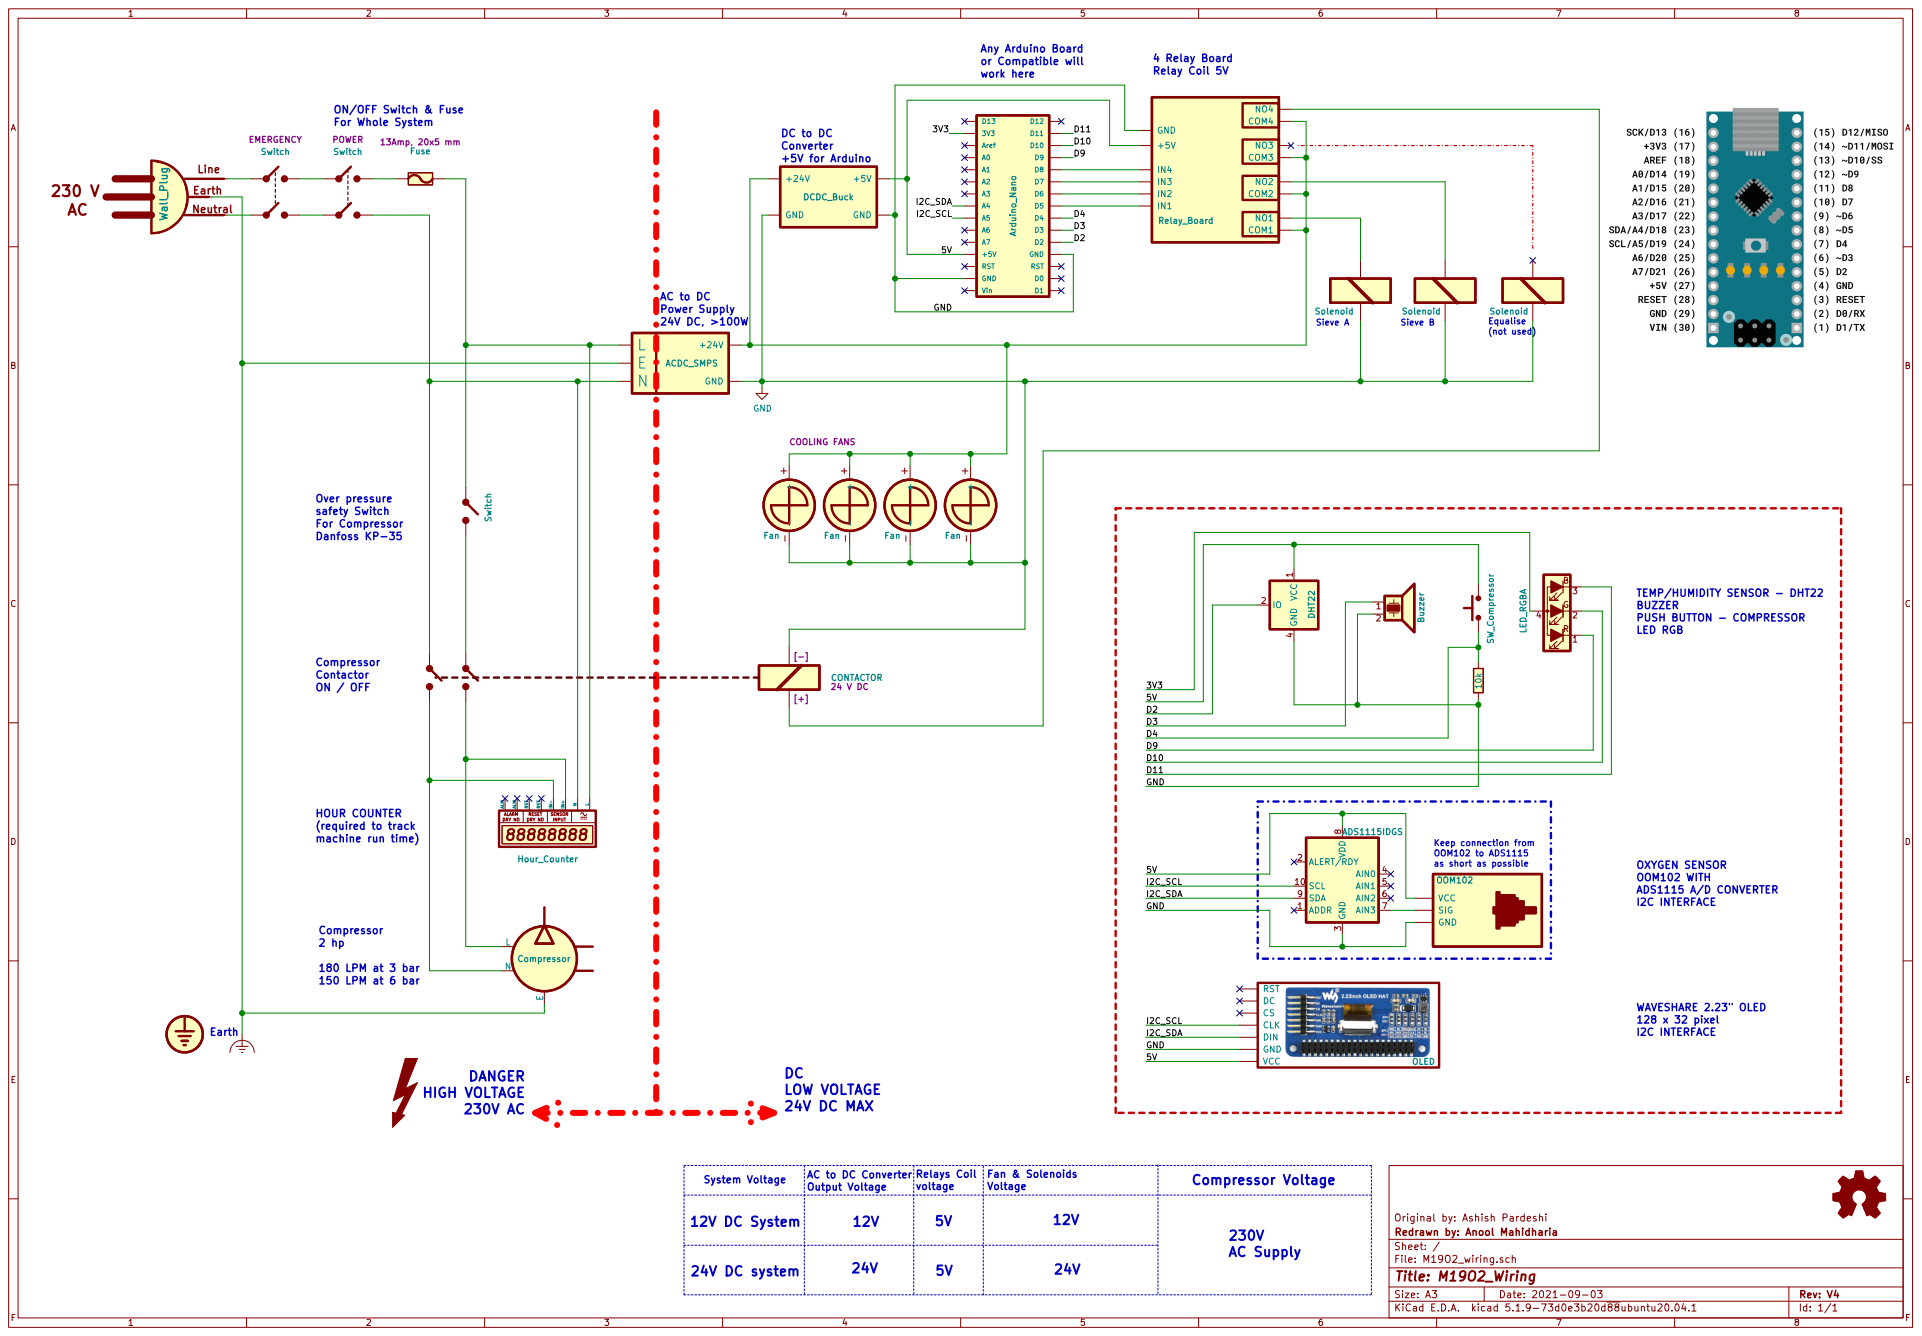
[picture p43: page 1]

Any Arduino Board
or Compatible will work here

ON/OFF Switch & Fuse
For Whole System
Switch POWER

TEMP/HUMIDITY SENSOR - DHT22 BUZZER

LED RGB HOUR COUNTER

D11 D10 D9 D4 D3 AC to DC Converter Output Voltage

Keep connection from
OOM102 to ADS1115
as short as possible
VCC OOM102

System Voltage | | Relays Coil voltage | Fan & Solenoids Voltage | Compressor Voltage

12V DC System | 12V | 5V | 12V | 230V AC Supply

File: M19O2_wiring.sch Sheet: / Redrawn by: Anool Mahidharia

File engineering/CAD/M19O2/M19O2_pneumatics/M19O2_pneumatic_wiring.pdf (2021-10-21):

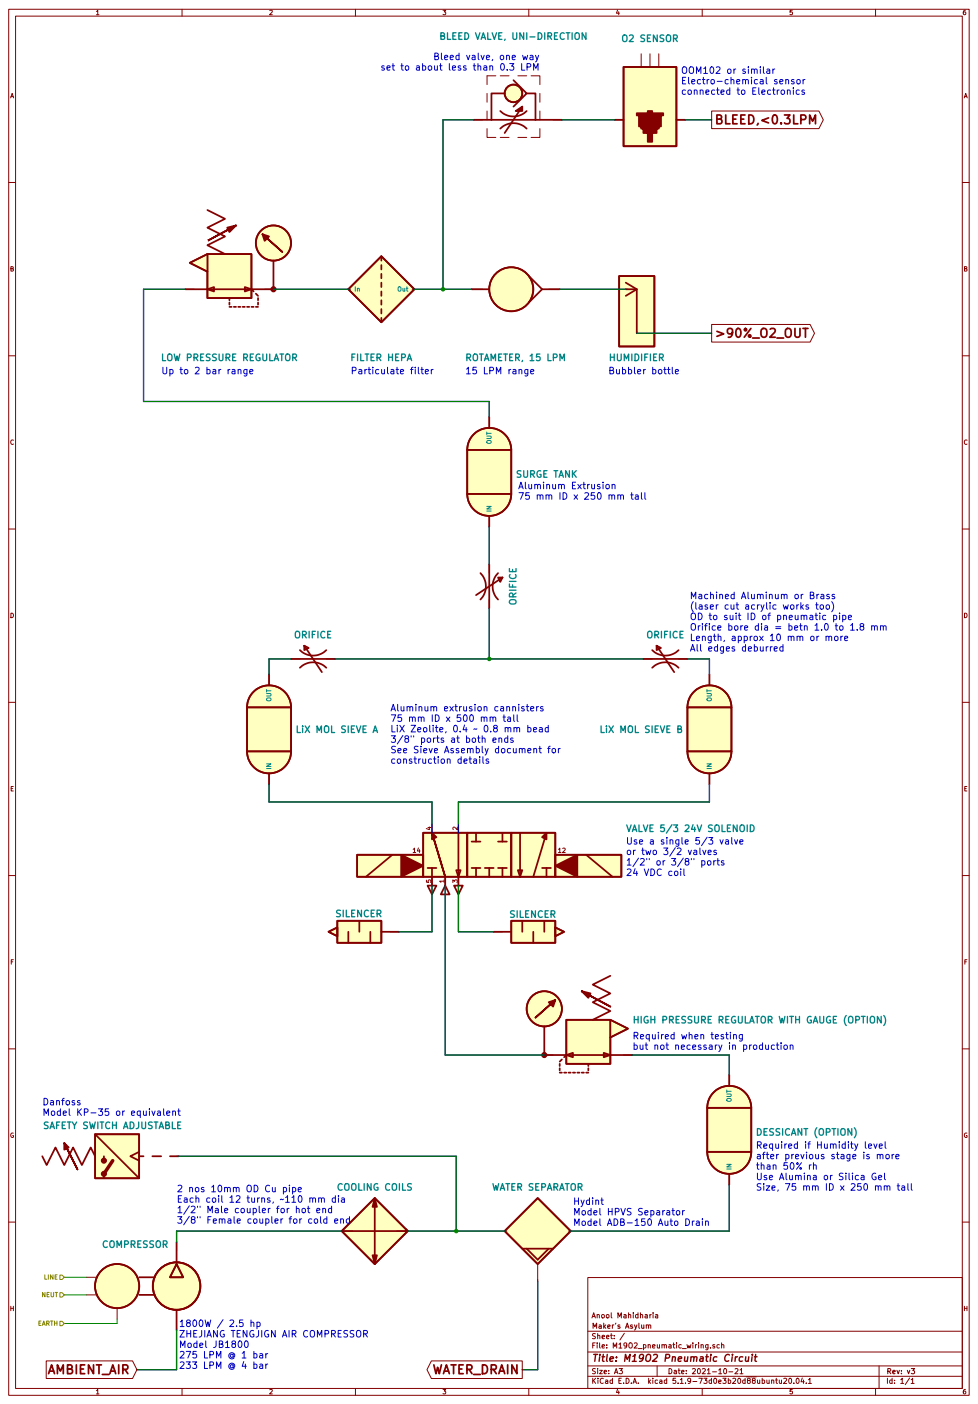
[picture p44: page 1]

Bleed valve, one way

set to about less than 0.3 LPM

SURGE TANK
Aluminum Extrusion
75 mm ID x 250 mm tall

Machined Aluminum or Brass
(laser cut acrylic works too)
OD to suit ID of pneumatic pipe
Orifice bore dia = betn 1.0 to 1.8 mm
Length, approx 10 mm or more
All edges deburred

LiX MOL SIEVE B IN OUT

Aluminum extrusion cannisters
75 mm ID x 500 mm tall
LiX Zeolite, 0.4 0.8 mm bead
3/8" ports at both ends
See Sieve Assembly document for
construction details

HIGH PRESSURE REGULATOR WITH GAUGE (OPTION)
Required when testing
but not necessary in production

Danfoss
Model KP-35 or equivalent
SAFETY SWITCH ADJUSTABLE

DESSICANT (OPTION)
Required if Humidity level
after previous stage is more
than 50% rh
Use Alumina or Silica Gel
Size, 75 mm ID x 250 mm tall

Anool Mahidharia COOLING COILS

2 nos 10mm OD Cu pipe
Each coil 12 turns, 110 mm dia
1/2" Male coupler for hot end
3/8" Female coupler for cold end

Hydint
Model HPVS Separator
Model ADB-150 Auto Drain

ZHEJIANG TENGJIGN AIR COMPRESSOR
Model JB1800
275 LPM @ 1 bar
233 LPM @ 4 bar

File: M19O2_pneumatic_wiring.sch Sheet: / Maker's Asylum

Id: 1/1 Title: M19O2 Pneumatic Circuit

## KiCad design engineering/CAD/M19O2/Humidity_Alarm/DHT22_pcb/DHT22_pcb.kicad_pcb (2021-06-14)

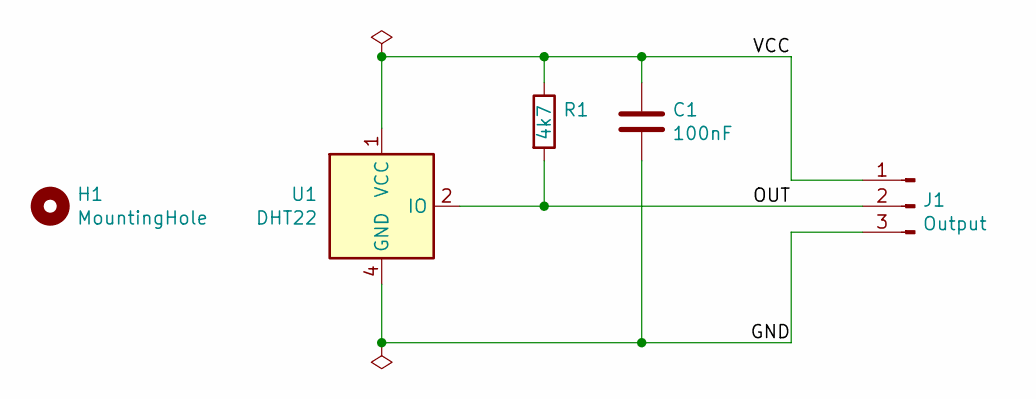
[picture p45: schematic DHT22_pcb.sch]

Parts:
C1: 100nF; C_0402_1005Metric
H1: MountingHole; MountingHole_2.2mm_M2_Pad_Via
J1: Output; PinHeader_1x03_P2.54mm_Vertical
R1: 4k7; R_0402_1005Metric
U1: DHT22; Aosong_DHT22_horiz

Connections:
/GND: C1.2, J1.3, U1.4 (GND)
/OUT: J1.2, R1.2, U1.2 (IO)
/VCC: C1.1, J1.1, R1.1, U1.1 (VCC)

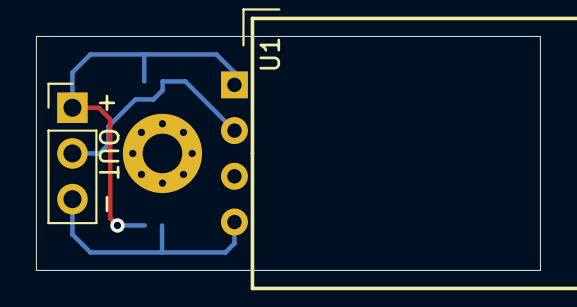
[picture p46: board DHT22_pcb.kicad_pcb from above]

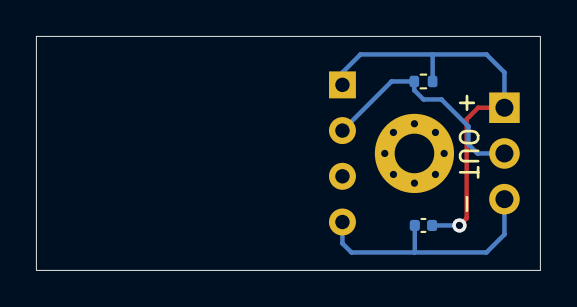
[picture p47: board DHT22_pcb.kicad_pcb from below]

Board: 2 copper layers, 28.0 x 13.0 mm, 5 parts (2 on the bottom side), 3 nets.

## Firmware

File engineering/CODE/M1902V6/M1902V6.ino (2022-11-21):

/* SCHEMATIC****************
   Relay pins:
   SIEVE A- D5
   SIEVE B- D6
   EQ_VALVE- D7 //NOT CONNECTED
   RELAY 4- D8 //For the compressor relay
   BUTTON - D4 //To turn on/off the compressor
   DHT    - D2
   Buzzer - D3

   RGB LED- D9: RED, D10: GREEN, D11: BLUE
   OLED   - DIN(SDA): A4, SCL: A5
*/

//Libraries
//****************************************************************
#include <DHT.h>
#include <SPI.h>
#include <Wire.h>
#include <Filter.h>                      //  https://www.megunolink.com/documentation/arduino-libraries/exponential-filter/
#include <Adafruit_GFX.h>
#include <Adafruit_SSD1305.h>
#include <Adafruit_ADS1015.h>

// I2C DISPLAY
//****************************************************************
#define OLED_RESET -1          //ARDUINO RESET PIN
#define SCREEN_ADDRESS 0x3C
Adafruit_SSD1305 display(128, 32, &Wire, OLED_RESET);


//DHT PARAMETERS
//****************************************************************
#define DHTPIN 2
#define DHTTYPE DHT22       // DHT 22
DHT dht(DHTPIN, DHTTYPE);


//ADC PARAMETERS FOR O2 CONCNTRATION
//****************************************************************
Adafruit_ADS1115 ads;
int adc0;                           //sensor connected on adc 0 pin
int O2;                           //variable to store o2 concentration
float factor;                       //multiplication factor to convert adc values in O2 concentration
const float multiplier = 0.1875;   //ADC 1 bit = 0.1875mV , ADC set to default gain
float O2_SMOOTH;                    //Filtered value
ExponentialFilter<float> O2_FILTERED(20, 20.9);   // the <float> makes a filter for float numbers // 20 is the weight (20 => 20%) // 20.9 is the initial value of the filter


//DIGITAL PIN ASSIGNMENTS
//****************************************************************
#define RED 9                       //RED LED
#define GREEN 10                    //GREEN LED
#define BLUE 11                     //BLUE LED
#define BUZZER 3                    //BUZZER PIN
#define BUTTON_PIN 4                //BUTTON PIN FOR CONTACTOR RELAY
#define SIEVE_A_PIN 5               //SIEVE A PIN
#define SIEVE_B_PIN 6               //SIEVE B PIN
#define EQ_VALVE_PIN 7             //EQULIZATION VALVE PIN
#define COMP_RELAY 8                //COMP RELAY


//VARIABLES
//****************************************************************
int h;                    //humidity
int t;                    //temperature

unsigned long prevCycleTime = millis();
int     prevCycle = 6;
unsigned long waitTime = 0;

bool state = HIGH;           // the current state of the output pin
int reading;                 // the current reading from the input pin
bool previous = LOW;
unsigned long Time = 0;      // the last time the output pin was toggled
const int debounce = 200;

//Set delay timing here
//**************************************************************************
const int S_ON_Eq_OFF = 3500;     //One sieve on, and equalisation valve off
const int S_ON_Eq_ON = 450;       //One sieve on, and euqialisation valve on
const int BS_ON_Eq_ON = 700;     //all valves low


//**************************************************************************
void setup() {
  Serial.begin(9600);       //serial communication for debugging
  Serial.println("Starting the machine");
  dht.begin();              //start DHT communication

  //check the display
  if ( ! display.begin(0x3C) ) {
    Serial.println("Unable to initialize OLED");
    while (1) yield();

  }
  display.clearDisplay();   // clears the screen and buffer
  delay(1000);
  display.clearDisplay();

  // SET PIN MODE FOR PINS IN PROGRAM
  //**************************************************************************
  pinMode(SIEVE_A_PIN, OUTPUT);
  pinMode(SIEVE_B_PIN, OUTPUT);
  pinMode(EQ_VALVE_PIN, OUTPUT);

  //define pins as input &output
  pinMode(RED, OUTPUT);
  pinMode(GREEN, OUTPUT);
  pinMode(BLUE, OUTPUT);

  pinMode(BUZZER, OUTPUT);
  pinMode(BUTTON_PIN, INPUT);
  pinMode(COMP_RELAY, OUTPUT);

  //Set initial states here
  //**************************************************************************
  //set SIEVE pins to LOW(turn off the relays)
  digitalWrite(SIEVE_A_PIN, HIGH);
  digitalWrite(SIEVE_B_PIN, HIGH);
  digitalWrite(EQ_VALVE_PIN, HIGH);

  //Set LED pins to LOW(turn off the LEDs)
  //**************************************************************************
  digitalWrite(RED, HIGH);
  digitalWrite(GREEN, HIGH);
  digitalWrite(BLUE, HIGH);

  //ADC values
  int adc_ambAirValue = ads.readADC_SingleEnded(0);  //adc value in ambient air
  if (adc_ambAirValue > 85) {
    factor = 3.82;
  } else {
    factor = adc_ambAirValue / 20.9;                   //slope 78.9 - 20.9% - 14.8mV ::: 372.26 - 98.6% - 69.8mv
  } 
  //Serial.println(adc_ambAirValue);
  //  float adc_maxValue = 100 * factor;
  //Serial.println(adc_ambAirValue);
  //  Serial.print('\t');
  //  Serial.print(factor);
  //  Serial.print('\t');
  //  Serial.println(adc_maxValue);
}

void loop() {
  COMP_SWITCH();       //turn on/off the compressor
  RUN_CYCLE();         //activate the sieves
  GET_TEMP();          //get the temperature and humidity
  //ALARM(h);            //set led colors and trigger alarm
  O2_CONCENTRATION();  //Calculate o2 concentration
  DISPLAY_DATA();      //display readings
}

void RUN_CYCLE() {
  //CYCLE 1
  //*****************************************************
  if ((millis() - prevCycleTime >= waitTime) && (prevCycle == 6)) {
    //Serial.println("Cycle 1");
    digitalWrite(SIEVE_A_PIN, LOW);
    digitalWrite(SIEVE_B_PIN, HIGH);
    digitalWrite(EQ_VALVE_PIN, HIGH);
    Serial.println("SEIVE A: ON, SEIVE B: OFF, EQ : OFF");
    prevCycleTime = millis();
    prevCycle = 1;
    waitTime = S_ON_Eq_OFF;
  }

  //CYCLE2
  //****************************************************
  if ((millis() - prevCycleTime >= waitTime) && (prevCycle == 1)) {
    //Serial.println("Cycle 2");
    digitalWrite(EQ_VALVE_PIN, LOW);
    Serial.println("SEIVE A: ON, SEIVE B: OFF, EQ : ON");
    prevCycleTime = millis();
    prevCycle = 2;
    waitTime = S_ON_Eq_ON;
  }

  //CYCLE 3
  //****************************************************
  if ((millis() - prevCycleTime >= waitTime) && (prevCycle == 2)) {
    //Serial.println("Cycle 3");
    digitalWrite(SIEVE_B_PIN, LOW);
    Serial.println("SEIVE A: ON, SEIVE B: ON, EQ : ON");
    prevCycleTime = millis();
    prevCycle = 3;
    waitTime = BS_ON_Eq_ON;
  }

  //CYCLE 4
  //***************************************************
  if ((millis() - prevCycleTime >= waitTime) && (prevCycle == 3)) {
    //Serial.println("Cycle 4");
    digitalWrite(SIEVE_A_PIN, HIGH);
    digitalWrite(EQ_VALVE_PIN, HIGH);
    Serial.println("SEIVE A: OFF, SEIVE B: ON, EQ: OFF");
    prevCycleTime = millis();
    prevCycle = 4;
    waitTime = S_ON_Eq_OFF;
  }

  //CYCLE 5
  //*****************************************************
  if ((millis() - prevCycleTime >= waitTime) && (prevCycle == 4)) {
    //Serial.println("Cycle 4");
    digitalWrite(EQ_VALVE_PIN, LOW);
    Serial.println("SEIVE A: OF, SEIVE B: ON, EQ : ON");
    prevCycleTime = millis();
    prevCycle = 5;
    waitTime = S_ON_Eq_ON;
  }

  //CYCLE6
  //****************************************************
  if ((millis() - prevCycleTime >= waitTime) && (prevCycle == 5)) {
    //Serial.println("Cycle 5");
    digitalWrite(SIEVE_A_PIN, HIGH);
    Serial.println("SEIVE A: ON, SEIVE B: ON, EQ : ON");
    prevCycleTime = millis();
    prevCycle = 6;
    waitTime = BS_ON_Eq_ON;
  }
}

//GET TEMPERATURE FROM THE DHT SENSOR
//**************************************************************************
void GET_TEMP() {
  h = dht.readHumidity();
  t = dht.readTemperature();
  //  Serial.println(h);
  //  Serial.println(t);
  if (isnan(h) || isnan(t)) {
    Serial.println(F("Failed to read from DHT sensor!"));
    digitalWrite(RED, LOW);
    digitalWrite(GREEN, LOW);
    digitalWrite(BLUE, LOW);
    return;
  }
}

//CONTROL THE COMPRESSOR RELAY FROM COMPRESSOR SWITCH
//**************************************************************************
void COMP_SWITCH() {
  reading = digitalRead(BUTTON_PIN);

  if (reading == HIGH && previous == LOW && millis() - Time > debounce) {
    if (state == HIGH) {
      state = LOW;
    }
    else {
      state = HIGH;
    }
    Time = millis();
  }

  digitalWrite(COMP_RELAY, state);
  previous = reading;
}


//DISPLAY READINGS ON THE SCREEN
//**************************************************************************
void DISPLAY_DATA() {
  display.clearDisplay();             //clear the display
  display.setTextSize(1);             //set text size, 1 is 10 pixel height
  display.setTextColor(WHITE);        //set color
  display.setCursor(0, 0);
  display.println("TEMP: ");          //print Temp:

  display.setCursor(30, 0);
  display.print(t, 0);              //print the temperature value, without decimal points
  display.setCursor(45, 0);
  if (t < 30) {
    display.println("norm");
  } else if (t > 30 && t <= 40) {
    display.println("chk");
  } else if (t > 40 && t <= 45) {
    display.println("high");
  } else if (t > 45) {
    display.println("warn");
  }

  display.setCursor(80, 0);
  display.println("HUM: ");            //print Hum :

  display.setCursor(105, 0);
  display.print(h, 0);              //print the humidity value, without decimal points

  display.setCursor(0, 12);
  display.println("O2% : ");

  display.setCursor(30, 12);
  if (O2_SMOOTH <= 100) {
    display.println(O2_SMOOTH, 0);
  }
  else {
    display.println("ERROR");
  }

  display.setCursor(70, 12);
  display.println("COMP: ");

  display.setCursor(100, 12);
  if (state == HIGH) {
    display.println("OFF");           //relays have reversed logic
  } else {
    display.println("ON");            //relays have reversed logic
  }

  display.display();                  //display data
}


//CALCULATE THE O2 CONCENTRATION
//**************************************************************************
void O2_CONCENTRATION() {
  adc0 = ads.readADC_SingleEnded(0); // Read ADC value from ADS1115

  //  Serial.println(factor);
  //  Serial.print("Analog pin 0: ");
  //Serial.println(adc0 * multiplier);

  //O2 = map(adc0, 80, 350, 20, 100);
  O2 = adc0 / factor;
  O2_FILTERED.Filter(O2);            //Calculate the filtered value
  O2_SMOOTH = O2_FILTERED.Current(); //calculate current filtered value

  //  Serial.println(O2_SMOOTH);
  if (O2_SMOOTH > 100 && O2_SMOOTH < 20) {
    Serial.println("Error reading oxygen percent");
  }
}


//CHANGE LED COLOR BASED ON O2 CONCENTRATION
//**************************************************************************
void ALARM(int h) {                 // turn on red if o2 conc. is less than 80%, blue for 80-90%, green for more than 90%
  if (O2_SMOOTH < 80) {
    analogWrite(RED, 180);          //common anode, 255 to turn off and 0 to turn on
    analogWrite(BLUE, 255);
    analogWrite(GREEN, 255);
  }

  else if (O2_SMOOTH >= 80 && O2_SMOOTH <= 90) {
    analogWrite(RED, 255);
    analogWrite(BLUE, 180);
    analogWrite(GREEN, 255);
  }

  else if (O2_SMOOTH > 90) {
    analogWrite(GREEN, 180);
    analogWrite(BLUE, 255);
    analogWrite(RED, 255);
  }

  else {
    analogWrite(RED, 255);
    analogWrite(GREEN, 255);
    analogWrite(BLUE, 255);
  }
}

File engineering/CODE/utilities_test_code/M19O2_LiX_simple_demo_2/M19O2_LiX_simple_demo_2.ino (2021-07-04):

/* SCHEMATIC****************
   I/O pins:
   DHT       - D2  // Temp/rH sensor
   Buzzer    - D3  // Direct to GPIO
   BUTTON    - D4  // Turns compressor ON/OFF
   SIEVE A   - D5  // Relay #1
   SIEVE B   - D6  // Relay #2
   RELAY 3   - D7  // Relay #3 NOT CONNECTED
   RELAY 4   - D8  // Relay #4 Compressor
   RGB LED   - Common Anode, to 3V3 without resistor
               D9  // RED
               D10 // GREEN
               D11 // BLUE
   I2C         A4  // SDA
   I2C         A5  // SCL
   OLED      - I2C ADDR 0x3C // SSD1305 controller, 2.23" OLED HAT 128*32 resolution
   O2 Sensor - I2C ADDR 0x48 // OOM102, with 3 pin header + ADS1115 ADC
*/

//Libraries
//****************************************************************
#include <EEPROM.h>
#include <DHT.h>
#include <SPI.h>
#include <Wire.h>
#include <Adafruit_GFX.h>
#include <Adafruit_SSD1305.h>
#include <Adafruit_ADS1X15.h>
#include "uptime.h"
#include "uptime_formatter.h"

// I2C DISPLAY
//****************************************************************
#define OLED_RESET -1        //ARDUINO RESET PIN
#define SCREEN_ADDRESS 0x3C

Adafruit_SSD1305 display(128, 32, &Wire, OLED_RESET);

//DHT PARAMETERS
//****************************************************************
#define DHTPIN 2
#define DHTTYPE DHT22       // DHT 22
DHT dht(DHTPIN, DHTTYPE);

//ADC PARAMETERS FOR O2 CONCENTRATION
//****************************************************************
Adafruit_ADS1115 ads;
int adc0;                           //sensor connected on adc 0 pin 
float o2percent;                    //variable to store o2 concentration
float factor;                       //multiplication factor to convert adc values in O2 concentration 
const float multiplier = 0.1875F;   //ADC 1 bit = 0.1875mV , ADC set to default gain

//DIGITAL PIN ASSIGNMENTS
//****************************************************************
#define RED 9                       //RED LED
#define GREEN 10                    //GREEN LED
#define BLUE 11                     //BLUE LED
#define BUZZER 3                    //BUZZER PIN
#define BUTTON_PIN 4                //BUTTON PIN FOR CONTACTOR RELAY
#define SIEVE_A_PIN 5               //SIEVE A PIN
#define SIEVE_B_PIN 6               //SIEVE B PIN
#define COMP_RELAY 8                //COMP RELAY

//VARIABLES
//****************************************************************
//Time update parameters
void RUN_CYCLE();
void UPDATE_TIME();

int currentTimeSeconds;
int noOfhours;
int noOfDays;
bool DaysWritten;
 
float h;                    //humidity
float t;                    //temperature

unsigned long prevCycleTime = millis();
int prevCycle = 4;
unsigned long waitTime = 0;

int state = HIGH;           // the current state of the output pin
int reading;                // the current reading from the input pin
int previous = LOW;         //
unsigned long time = 0;     // the last time the output pin was toggled
unsigned long debounce = 200UL;

//Set delay timing here
//**************************************************************************
int CYCLE_TIME = 4000;
int FLUSH_TIME = 850;
int PRODUCTION_TIME = CYCLE_TIME - 2 * FLUSH_TIME;

//**************************************************************************

void setup() {
  Serial.begin(9600);       //serial communication for debugging
  Serial.println("Starting the machine");
//  dht.begin();              //start DHT communication
//  EEPROM.begin();

//check the display
//  if ( ! display.begin(0x3C) ) {
//    Serial.println("Unable to initialize OLED");
//    while (1) yield();
//  }
//  display.clearDisplay();   // clears the screen and buffer
//  delay(1000);
//  display.clearDisplay();
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

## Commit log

2021-04-29 renamed images
    [Oxygen Sensor KE-25F3.SLDPRT, Oxygen Sensor KE-25F3.stp, TTGO T-Display.stp]
2021-04-30 Added README and starting CAD content
    [OxiKit_v22.FCStd]
2021-04-30 updated SD
    [OxiKit_v22.FCStd]
2021-05-01 Added valve step files to cad submodule
2021-05-01 Started FreeCAD Assembly of OxiKit v22
2021-05-01 Made frame FreeCAD assembly. Unconstrained. Added to parent assembly
2021-05-01 Updated CAD assembly of v22
2021-05-02 Updated tubing on freecad assembly
2021-05-02 Updated assembly - top solenoid fitting - reset tubes
2021-05-02 Updated tanks in assembly
2021-05-02 Updated assembly (unconstrained). Only tubing left.
2021-05-03 Merged and updated electronics folder.
    [Oxygen Sensor KE-25F3.SLDPRT, Oxygen Sensor KE-25F3.stp, TTGO T-Display.stp]
2021-05-19 Simplified structure. Removed submodules, for now.
    [0.25_MIP_to_CompressionElbow.FCStd, 0.25_MIP_to_CompressionElbow.step, 0.25_MPT_to_0.375_Push.FCStd, 0.25_MPT_to_0.375_Push.step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]
2021-05-19 [FEATURE] Restructuring.
    [0.25_MIP_to_CompressionElbow.FCStd, 0.25_MIP_to_CompressionElbow.step, 0.25_MPT_to_0.375_Push.FCStd, 0.25_MPT_to_0.375_Push.step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]
2021-05-21 nafion tubes paper
2021-05-23 [FIX] rearrange
    [0.25_MIP_to_CompressionElbow.FCStd, 0.25_MIP_to_CompressionElbow.step, 0.25_MPT_to_0.375_Push.FCStd, 0.25_MPT_to_0.375_Push.step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]
2021-06-10 added O2 sensor adapter
    [3_8th_thread_nut_job_20140410-16170-mk5hsl-0.stl, OOM Adapter.stl, OOM_T_Joint.stl]
2021-06-12 added LiX zeolite timing code WIP
    [Seed_Storage_Box_Air_Tight_Lid.stl, Seed_Storage_Box_Body.stl, Seed_Storage_Box_Body_With_Separator.stl, Seed_Storage_Box_Ventilated_Lid.stl]
2021-06-14 added Sieve aluminum extrusion assembly in CAD folder WIP
    [3_8_push_fit.stp, DHT22_T_sensor.step, DHT22_pcb.kicad_pcb, DHT22_pcb.sch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]
2021-06-27 Sieve Assembly, Sieve Compression Jig, Humidity Sensor housings etc
    [120mm_fan.stp, 120mm_fan_baffle.FCStd, 120mm_fan_grill.step, Case.step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]
2021-06-29 folder restructuring and added M19O2 wiring in Electronics
    [0.25_MIP_to_CompressionElbow.FCStd, 0.25_MIP_to_CompressionElbow.step, 0.25_MPT_to_0.375_Push.FCStd, 0.25_MPT_to_0.375_Push.step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]
2021-06-30 started M19O2_v4 CAD assy
    [120mm_fan.stp, Case.step, Fuse-Holder-Small.stp, Humidifier.step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]
2021-07-04 finished M19O2_v4 CAD assy
    [Humidifier_with_flowmeter.step, Janatics-R14.step, M19O2_v4_moisture_bracket.dxf, acp_back.dxf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]
2021-07-05 M19O2 pneumatic circuit added
2021-07-09 M19O2 CAD updates
    [acp_water_sep_back.dxf, acp_water_sep_side.dxf, acp_water_sep_top.dxf, acrylic_outer_right.dxf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]
2021-07-16 M19O2 pneumatic wiring update
    [M19O2_pneumatic_wiring.kicad_pcb, M19O2_pneumatic_wiring.sch, sieve_assembly_v3.FCStd, sieve_endcap.step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]
2021-07-17 M19O2 added O2 sensor measurement code and main code
    [O2_conc_limits_of_PSA.ods]
2021-07-26 M19O2 Datasheet & Instruction Manual update
    [sieve_assembly_v3.FCStd]
2021-07-30 M19O2 Oxygen sensor mount
    M19O2 Oxygen sensor mount
    [M19O2_v4_assembly-O2_sensor.SLDPRT, oxysensor block.STL]
2021-08-06 M19O2 extracted assembly images from CAD
    [Janatics-WP221.step, sieve_assembly_v3.FCStd]
2021-08-13 M19O2 several incremental updates
    [Janatics-elbow.step, sieve_assembly_v3.FCStd]
2021-08-13 M19O2 assembly manual added
2021-08-19 M19O2 added moisture separator and auto drain STEP files
    [hydint_auto_drain.step, hydint_moisture_separator_01.step, hydint_moisture_separator_02.step]
2021-09-04 big push - added Hour Counter, and modified all renders and drawings
    [M19O2_v4_moisture_bracket.dxf, M19O2_wiring.sch, button.stl, compressor_sw_plug_Cap.stl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]
2021-09-17 some updates
    [Janatics-ASC_18_silencer.step, Janatics-ASC_silencer.step, Janatics-DSSC60_solenoid.step, Janatics-WP221.step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]
2021-10-21 documentation updates
    [M19O2_pneumatic_pictorial.sch, M19O2_pneumatic_wiring.sch]
2022-11-21 added hi-res 3D CAD renders
    [acr_sieve_bracket_dia71-01.dxf, acr_sieve_bracket_dia71-02.dxf, acr_sieve_bracket_dia71.FCStd]
